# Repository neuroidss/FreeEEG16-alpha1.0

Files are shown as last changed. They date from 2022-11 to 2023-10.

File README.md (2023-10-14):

# FreeEEG16-alpha1.0 TEST FAILED
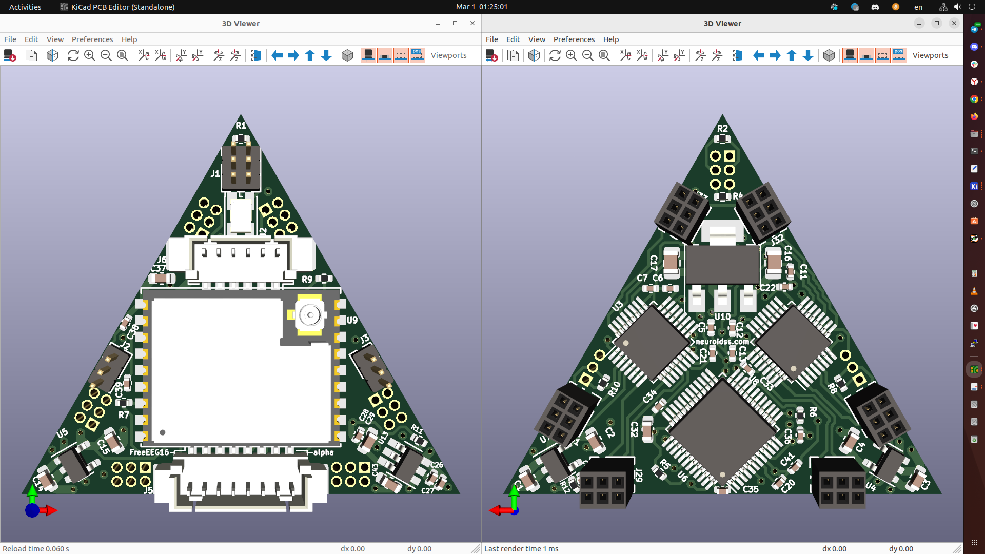
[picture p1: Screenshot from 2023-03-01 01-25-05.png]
FreeEEG16-alpha

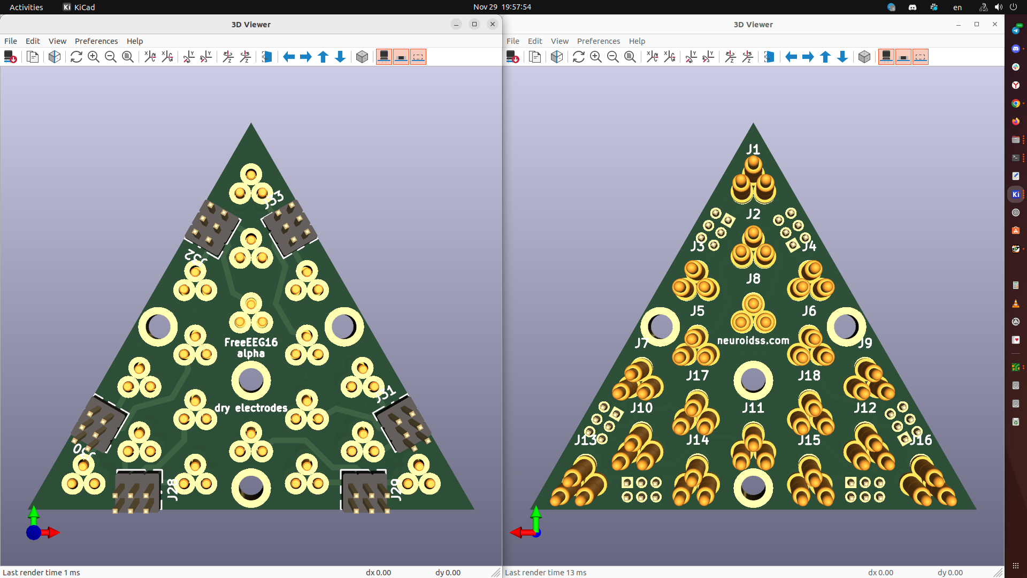
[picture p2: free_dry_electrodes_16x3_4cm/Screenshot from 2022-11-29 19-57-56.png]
free_dry_electrodes_16x3_4cm


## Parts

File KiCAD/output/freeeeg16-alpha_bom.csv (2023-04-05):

Id | Designator | Footprint | Quantity | Designation | Supplier and ref
1 | C14,C15,C3,C2,C1,C4 | C_0603_1608Metric | 6 | 2.2u | CL10A225KO8NNNC | GRM188R71A225KE15D
2 | C29,C37 | C_0603_1608Metric | 2 | 10u | GRM188R60J106ME47D
3 | R13,R9,R7 | R_0402_1005Metric | 3 | 10k | RC0402JR-0710KL
4 | C39,C27,C5,C11,C13,C7 | C_0402_1005Metric | 6 | 1u | CL05A105KO5NNNC
5 | C38,C26,C28,C36,C40,C22,C20,C35,C21,C33,C41,C34 | C_0402_1005Metric | 12 | 100n | CL05B104KO5NNNC
6 | R11,R1,R8,R4,R2,R10 | R_0402_1005Metric | 6 | 0 | RC0402JR-070RL
7 | J1 | PinHeader_2x03_P1.27mm_Vertical | 1 | Conn_02x03_Odd_Even | 20021111-00006T1LF
8 | C43 | C_0603_1608Metric | 1 | 10u DNP | DNP
9 | U5,U4,U7 | SOT-23-5 | 3 | LP5907 | LP5907MFX-3.3/NOPB
10 | U13 | SOT-23-6_Handsoldering | 1 | MAX6070AAUT12 | MAX6070AAUT12+T
11 | J5 | Molex_PicoBlade_53398-0871_1x08-1MP_P1.25mm_Vertical_cut | 1 | Conn_01x08 | 53398-0871
12 | J6 | Molex_PicoBlade_53398-0671_1x06-1MP_P1.25mm_Vertical | 1 | Conn_01x06 | 53398-0671
13 | J3,J2 | PinHeader_1x03_P1.27mm_Vertical | 2 | Conn_01x03 | TMS-103-02-L-S
14 | U2 | Oscillator_SMD_EuroQuartz_XO32-4Pin_3.2x2.5mm_HandSoldering_cut | 1 | 8.192MHz | ECS-2520MVLC-081.92-CN-TR | ECS-2520MVLC-081.92-BN-TR3 | ECS-2520MVLC-081.92-BN-TR | SIT8924BA-22-33E-8.192000G
15 | U9 | ESP32-C3-WROOM-02U | 1 | ESP32-C3-WROOM-02 | ESP32-C3-WROOM-02U-N4
16 | J29,J28,J31,J32,J33,J30 | PinSocket_2x03_P1.27mm_Vertical | 6 | Conn_02x03_Odd_Even | 20021311-00006T4LF
17 | R6,R5 | R_0402_1005Metric | 2 | 4k7 | RC0402JR-074K7L
18 | U6 | LQFP-48_7x7mm_P0.5mm | 1 | STM32F103CBTx | STM32F103C8T6 | GD32VF103CBT6 | CH32V103C8T6
19 | U10 | SOT-223-3_TabPin2 | 1 | AMS1117-3.3 | TLV1117-33IDCY | TLV1117-33IDCYG3
20 | C12,C6 | C_0402_1005Metric | 2 | 220n | CC0402KRX5R5BB224
21 | U3,U8 | LQFP-32_5x5mm_P0.5mm | 2 | ADS131M08IPBSR | ADS131M08IPBSR
22 | C16,C17 | C_0805_2012Metric | 2 | 22u | GRM21BR60J226ME39L
23 | C32 | C_0603_1608Metric | 1 | 4.7u | C0603C475K9PACTU
24 | R12 | R_0402_1005Metric | 1 | 0 DNP | DNP

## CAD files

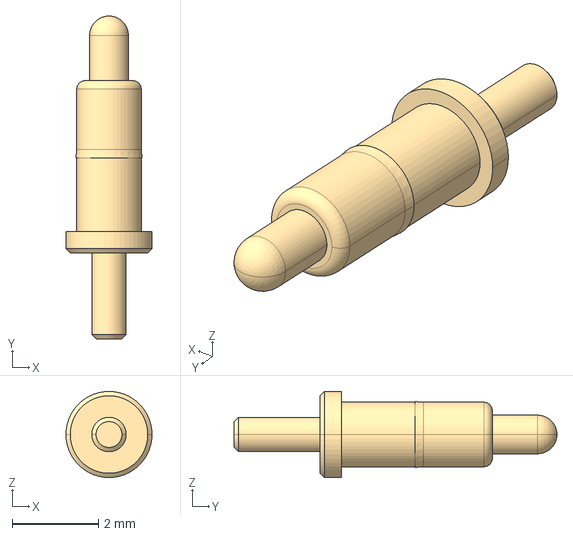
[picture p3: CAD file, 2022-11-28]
free_dry_electrodes_16x3_4cm/p70-2100045/p70-2100045.stp
2.00 x 7.50 x 2.00 mm

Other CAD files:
free_dry_electrodes_16x3_4cm/p70-2100045/p70-2100045.igs

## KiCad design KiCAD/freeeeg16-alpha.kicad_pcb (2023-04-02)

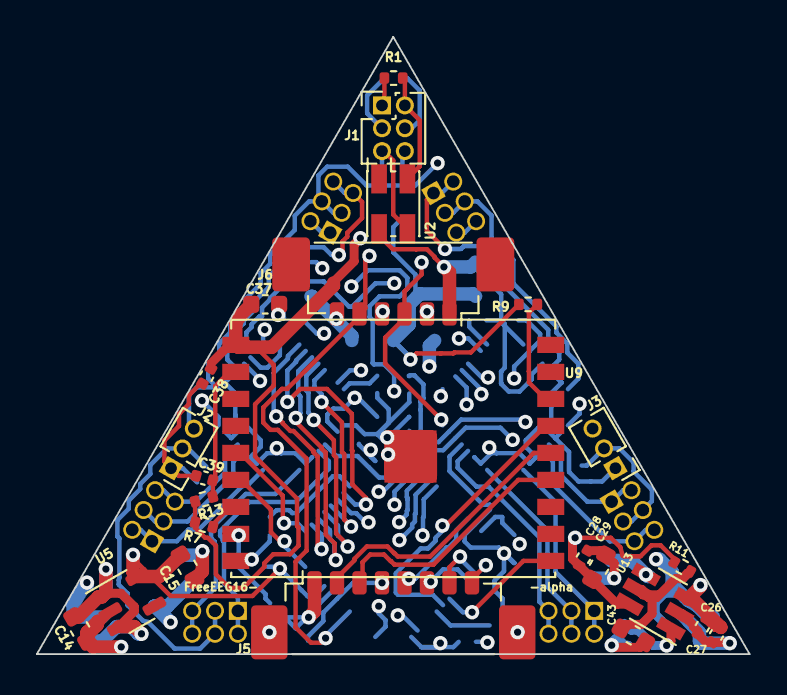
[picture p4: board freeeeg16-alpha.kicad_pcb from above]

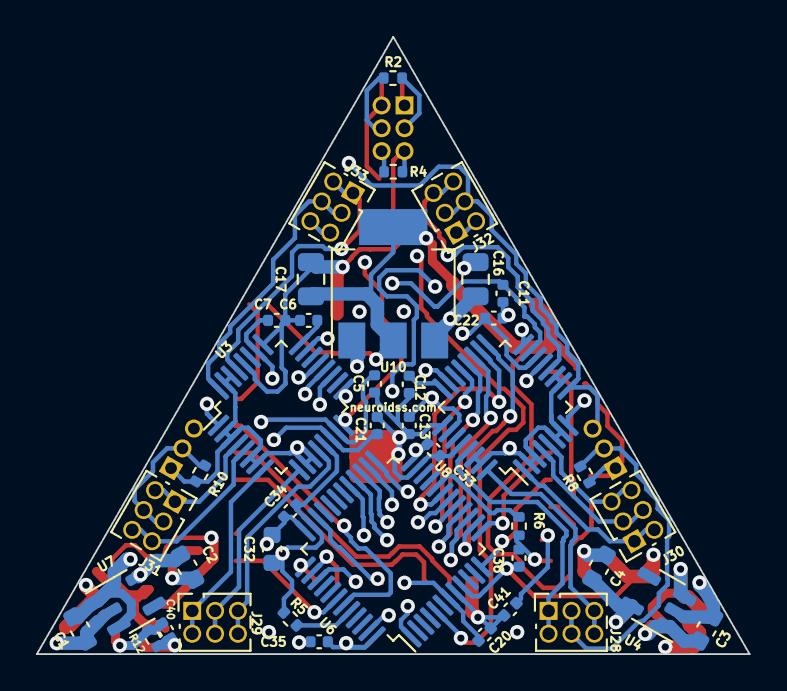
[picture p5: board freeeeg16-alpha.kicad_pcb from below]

Board: 4 copper layers, 39.6 x 34.3 mm, 65 parts (41 on the bottom side), 62 nets.

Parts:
C1, C2, C3, C4, C14, C15: 2.2u; C_0603_1608Metric
C5, C7, C11, C13, C27, C39: 1u; C_0402_1005Metric
C6, C12: 220n; C_0402_1005Metric
C16, C17: 22u; C_0805_2012Metric
C20, C21, C22, C26, C28, C33, C34, C35, C36, C38, C40, C41: 100n; C_0402_1005Metric
C29, C37: 10u; C_0603_1608Metric
C32: 4.7u; C_0603_1608Metric
C43: 10u DNP; C_0603_1608Metric
J1: Conn_02x03_Odd_Even; PinHeader_2x03_P1.27mm_Vertical
J2, J3: Conn_01x03; PinHeader_1x03_P1.27mm_Vertical
J5: Conn_01x08; Molex_PicoBlade_53398-0871_1x08-1MP_P1.25mm_Vertical_cut
J6: Conn_01x06; Molex_PicoBlade_53398-0671_1x06-1MP_P1.25mm_Vertical
J28, J29, J30, J31, J32, J33: Conn_02x03_Odd_Even; PinSocket_2x03_P1.27mm_Vertical
R1, R2, R4, R8, R10, R11: 0; R_0402_1005Metric
R5, R6: 4k7; R_0402_1005Metric
R7, R9, R13: 10k; R_0402_1005Metric
R12: 0 DNP; R_0402_1005Metric
U2: 8.192MHz; Oscillator_SMD_EuroQuartz_XO32-4Pin_3.2x2.5mm_HandSoldering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
U3, U8: ADS131M08IPBSR; LQFP-32_5x5mm_P0.5mm
U4, U5, U7: LP5907; SOT-23-5
U6: STM32F103CBTx; LQFP-48_7x7mm_P0.5mm
U9: ESP32-C3-WROOM-02; ESP32-C3-WROOM-02U
U10: AMS1117-3.3; SOT-223-3_TabPin2
U13: MAX6070AAUT12; SOT-23-6_Handsoldering

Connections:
3V3_1_IN: C1.1, C3.1, C14.1, C16.1, J6.6, U4.1 (IN), U4.3 (EN), U5.1 (IN), U5.3 (EN), U7.1 (IN), U7.3 (EN), U10.3 (VI)
3V3_2_GND: C1.2, C2.2, C3.2, C4.2, C5.2, C6.2, C7.2, C11.2, C12.2, C13.2, C14.2, C15.2, C16.2, C17.2, C20.1, C21.2, C22.2, C26.2, C27.2, C28.2, C29.2, C32.2, C33.2, C34.2, C35.2, C36.2, C37.2, C38.2, C39.1, C40.2, C41.1, C43.1, J2.1, J5.1, J6.1, R5.2, R6.2, R8.2, R12.2, U2.2 (GND), U3.13 (AGND), U3.25 (DGND), U3.28 (AGND), U4.2 (GND), U5.2 (GND), U6.8 (VSSA), U6.23 (VSS), U6.35 (VSS), U6.47 (VSS), U7.2 (GND), U8.13 (AGND), U8.25 (DGND), U8.28 (AGND), U9.9 (GND), U9.19 (GND), U10.1 (GND), U13.2 (GND)
3V3_5_OUT: C17.1, C37.1, C38.1, R7.2, R9.2, R13.2, U9.1 (3V3), U10.2 (VO)
/ADC1/24_CAP: C12.1, U8.24 (CAP)
/ADC2/24_CAP: C6.1, U3.24 (CAP)
/J17: J3.2, J31.3, J31.4, R10.1
/J18: J2.2, J28.3, J28.4, R8.1
/vref2/1_FILTER: C40.1, R12.1, U13.1 (FILTER)
ACC_5_VDDIO: C15.1, C32.1, C33.1, C34.1, C35.1, C36.1, J1.1, R1.1, U5.5 (OUT), U6.1 (VBAT), U6.9 (VDDA), U6.24 (VDD), U6.36 (VDD), U6.48 (VDD)
ACC_13_SCL: U6.42 (PB6), U9.10 (GPIO10)
ACC_14_SDA: U6.43 (PB7), U9.15 (GPIO3/ADC1_CH3)
ADC1_01_AIN2P: J30.1, J30.2, U8.1 (AIN2P)
ADC1_02_AIN2N: J3.1, J6.2, R10.2, U3.2 (AIN2N), U3.3 (AIN3N), U3.6 (AIN4N), U3.7 (AIN5N), U3.10 (AIN6N), U3.11 (AIN7N), U3.30 (AIN0N), U3.31 (AIN1N), U8.2 (AIN2N), U8.3 (AIN3N), U8.6 (AIN4N), U8.7 (AIN5N), U8.10 (AIN6N), U8.11 (AIN7N), U8.30 (AIN0N), U8.31 (AIN1N)
ADC1_04_AIN3P: J30.3, J30.4, U8.4 (AIN3P)
ADC1_05_AIN4P: J30.5, J30.6, U8.5 (AIN4P)
ADC1_08_AIN5P: J32.1, J32.2, U8.8 (AIN5P)
ADC1_09_AIN6P: J2.3, J3.3, J32.3, J32.4, U8.9 (AIN6P)
ADC1_12_AIN7P: J32.5, J32.6, U8.12 (AIN7P)
ADC1_14_REFIN: C21.1, C22.1, C28.1, C29.1, J6.4, R11.2, U3.14 (REFIN), U8.14 (REFIN), U13.6 (OUTF)
ADC1_15_AVDD: C2.1, C5.1, C11.1, C26.1, C27.1, U3.15 (AVDD), U7.5 (OUT), U8.15 (AVDD), U13.3 (EN), U13.4 (IN)
ADC1_16_SYNC/RESET: J1.4, J6.3, R2.2, U3.16 (SYNC/RESET), U8.16 (SYNC/RESET)
ADC1_17_CS: U6.14 (PA4), U8.17 (CS)
ADC1_18_DRDY: U6.19 (PB1), U8.18 (DRDY)
ADC1_19_SCLK: U6.15 (PA5), U8.19 (SCLK)
ADC1_20_DOUT: U6.16 (PA6), U8.20 (DOUT)
ADC1_21_DIN: U6.17 (PA7), U8.21 (DIN)
ADC1_23_XTAL1/CLKIN: U3.23 (XTAL1/CLKIN), U6.29 (PA8), U8.23 (XTAL1/CLKIN)
ADC1_26_DVDD: C4.1, C7.1, C13.1, U3.26 (DVDD), U4.5 (OUT), U8.26 (DVDD)
ADC1_29_AIN0P: J28.1, J28.2, U8.29 (AIN0P)
ADC1_32_AIN1P: J28.5, J28.6, U8.32 (AIN1P)
ADC2_01_AIN2P: J33.5, J33.6, U3.1 (AIN2P)
ADC2_04_AIN3P: J31.1, J31.2, U3.4 (AIN3P)
ADC2_05_AIN4P: J31.5, J31.6, U3.5 (AIN4P)
ADC2_08_AIN5P: J29.1, J29.2, U3.8 (AIN5P)
ADC2_09_AIN6P: J29.3, J29.4, U3.9 (AIN6P)
ADC2_12_AIN7P: J29.5, J29.6, U3.12 (AIN7P)
ADC2_17_CS: U3.17 (CS), U6.25 (PB12)
ADC2_19_SCLK: U3.19 (SCLK), U6.26 (PB13)
ADC2_20_DOUT: U3.20 (DOUT), U6.27 (PB14)
ADC2_21_DIN: U3.21 (DIN), U6.28 (PB15)
ADC2_29_AIN0P: J33.1, J33.2, U3.29 (AIN0P)
ADC2_32_AIN1P: J33.3, J33.4, U3.32 (AIN1P)
CRYSTAL_3_OUT: J1.5, R4.1, U2.3 (OUT)
CRYSTAL_4_Vin: J1.2, R1.2, U2.4 (Vin)
MCU_5_PDO0_RCC_OSC_IN: J1.6, J6.5, R4.2, U6.5 (PD0)
MCU_7_NRST: C20.2, J5.4, U6.7 (NRST)
MCU_12_PA2_USART2_TX: U6.12 (PA2), U9.6 (GPIO7)
MCU_13_PA3_USART2_RX: U6.13 (PA3), U9.5 (GPIO6)
MCU_18_PB0_ADC1_SYNC/RESET: J1.3, R2.1, U6.18 (PB0)
MCU_20_PB2_BOOT1: R6.1, U6.20 (PB2)
MCU_34_PA13_SYS_JTMS-SWDIO: J5.5, U6.34 (PA13)
MCU_37_PA14_SYS_JTCK-SWCLK: J5.8, U6.37 (PA14)
MCU_38_PA15_SYS_JTDI: J5.7, U6.38 (PA15)
MCU_39_PB3_SYS_JTDO-TRACESWO: J5.6, U6.39 (PB3)
MCU_44_BOOT0: R5.1, U6.44 (BOOT0)
unnamed: C43.2, R11.1, U13.5 (OUTS)
RADIO_2_EN: C39.2, R13.1, U9.2 (EN/CHIP_PU)
RADIO_7_GPIO8: R7.1, U9.7 (GPIO8)
RADIO_8_GPIO9: C41.2, U9.8 (GPIO9)
RADIO_13_GPIO18/USB_D-: J5.3, U9.13 (GPIO18/USB_D-)
RADIO_14_GPIO19/USB_D+: J5.2, U9.14 (GPIO19/USB_D+)
RADIO_16_GPIO2: R9.1, U9.16 (GPIO2/ADC1_CH2)

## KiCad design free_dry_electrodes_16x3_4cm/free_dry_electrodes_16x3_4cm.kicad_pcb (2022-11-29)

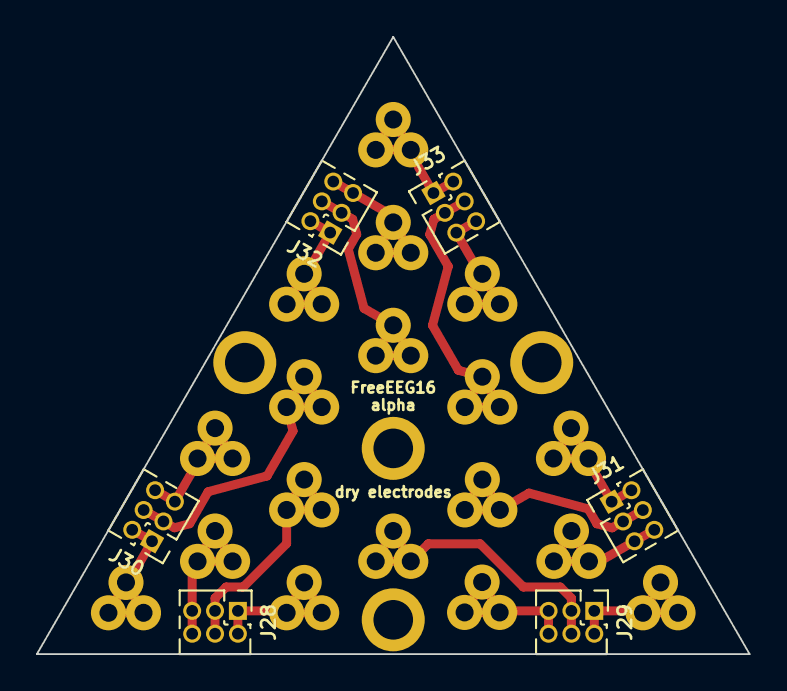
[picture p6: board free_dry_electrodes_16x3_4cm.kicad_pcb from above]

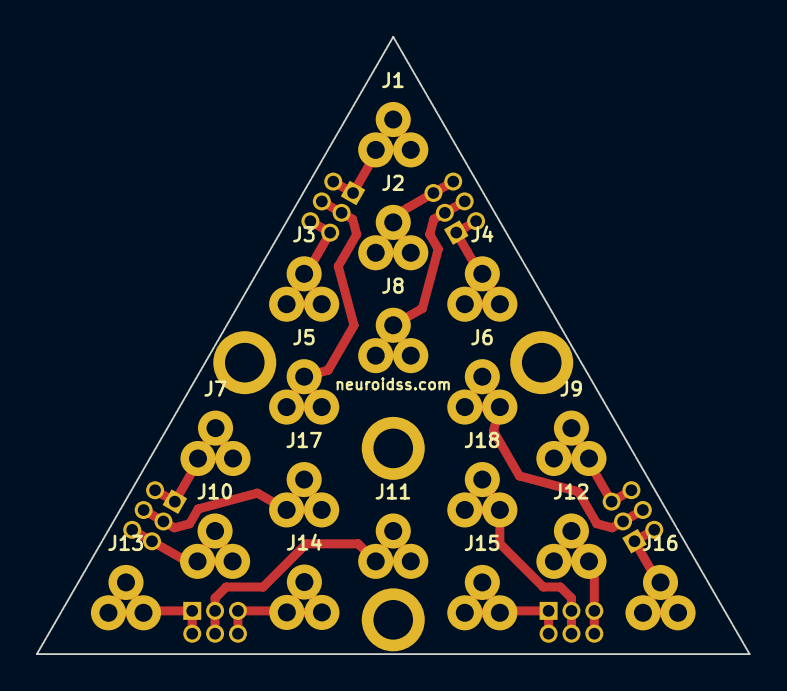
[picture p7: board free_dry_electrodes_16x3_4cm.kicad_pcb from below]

Board: 2 copper layers, 39.6 x 34.3 mm, 24 parts (18 on the bottom side), 18 nets.

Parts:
J1, J2, J3, J4, J5, J6, J7, J8, J9, J10, J11, J12, J13, J14, J15, J16, J17, J18: Conn_01x03; CPA_3_od4.5_d1.95_id1.0
J28, J29, J30, J31, J32, J33: Conn_02x03_Odd_Even; PinHeader_2x03_P1.27mm_Vertical

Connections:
/J1: J1.1, J1.2, J1.3, J33.1, J33.2
/J2: J2.1, J2.2, J2.3, J32.5, J32.6
/J3: J3.1, J3.2, J3.3, J33.5, J33.6
/J4: J4.1, J4.2, J4.3, J32.1, J32.2
/J5: J5.1, J5.2, J5.3, J33.3, J33.4
/J6: J6.1, J6.2, J6.3, J30.3, J30.4
/J7: J7.1, J7.2, J7.3, J31.1, J31.2
/J8: J8.1, J8.2, J8.3, J32.3, J32.4
/J9: J9.1, J9.2, J9.3, J30.5, J30.6
/J10: J10.1, J10.2, J10.3, J31.5, J31.6
/J11: J11.1, J11.2, J11.3, J29.3, J29.4
/J12: J12.1, J12.2, J12.3, J28.5, J28.6
/J13: J13.1, J13.2, J13.3, J29.1, J29.2
/J14: J14.1, J14.2, J14.3, J29.5, J29.6
/J15: J15.1, J15.2, J15.3, J28.1, J28.2
/J16: J16.1, J16.2, J16.3, J30.1, J30.2
/J17: J17.1, J17.2, J17.3, J31.3, J31.4
/J18: J18.1, J18.2, J18.3, J28.3, J28.4

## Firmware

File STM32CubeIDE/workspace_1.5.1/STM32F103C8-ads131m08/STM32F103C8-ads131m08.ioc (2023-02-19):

#MicroXplorer Configuration settings - do not modify
Dma.Request0=USART2_TX
Dma.Request1=USART2_RX
Dma.Request2=SPI1_RX
Dma.Request3=SPI1_TX
Dma.Request4=SPI2_RX
Dma.Request5=SPI2_TX
Dma.RequestsNb=6
Dma.SPI1_RX.2.Direction=DMA_PERIPH_TO_MEMORY
Dma.SPI1_RX.2.Instance=DMA1_Channel2
Dma.SPI1_RX.2.MemDataAlignment=DMA_MDATAALIGN_BYTE
Dma.SPI1_RX.2.MemInc=DMA_MINC_ENABLE
Dma.SPI1_RX.2.Mode=DMA_NORMAL
Dma.SPI1_RX.2.PeriphDataAlignment=DMA_PDATAALIGN_BYTE
Dma.SPI1_RX.2.PeriphInc=DMA_PINC_DISABLE
Dma.SPI1_RX.2.Priority=DMA_PRIORITY_LOW
Dma.SPI1_RX.2.RequestParameters=Instance,Direction,PeriphInc,MemInc,PeriphDataAlignment,MemDataAlignment,Mode,Priority
Dma.SPI1_TX.3.Direction=DMA_MEMORY_TO_PERIPH
Dma.SPI1_TX.3.Instance=DMA1_Channel3
Dma.SPI1_TX.3.MemDataAlignment=DMA_MDATAALIGN_BYTE
Dma.SPI1_TX.3.MemInc=DMA_MINC_ENABLE
Dma.SPI1_TX.3.Mode=DMA_NORMAL
Dma.SPI1_TX.3.PeriphDataAlignment=DMA_PDATAALIGN_BYTE
Dma.SPI1_TX.3.PeriphInc=DMA_PINC_DISABLE
Dma.SPI1_TX.3.Priority=DMA_PRIORITY_LOW
Dma.SPI1_TX.3.RequestParameters=Instance,Direction,PeriphInc,MemInc,PeriphDataAlignment,MemDataAlignment,Mode,Priority
Dma.SPI2_RX.4.Direction=DMA_PERIPH_TO_MEMORY
Dma.SPI2_RX.4.Instance=DMA1_Channel4
Dma.SPI2_RX.4.MemDataAlignment=DMA_MDATAALIGN_BYTE
Dma.SPI2_RX.4.MemInc=DMA_MINC_ENABLE
Dma.SPI2_RX.4.Mode=DMA_NORMAL
Dma.SPI2_RX.4.PeriphDataAlignment=DMA_PDATAALIGN_BYTE
Dma.SPI2_RX.4.PeriphInc=DMA_PINC_DISABLE
Dma.SPI2_RX.4.Priority=DMA_PRIORITY_LOW
Dma.SPI2_RX.4.RequestParameters=Instance,Direction,PeriphInc,MemInc,PeriphDataAlignment,MemDataAlignment,Mode,Priority
Dma.SPI2_TX.5.Direction=DMA_MEMORY_TO_PERIPH
Dma.SPI2_TX.5.Instance=DMA1_Channel5
Dma.SPI2_TX.5.MemDataAlignment=DMA_MDATAALIGN_BYTE
Dma.SPI2_TX.5.MemInc=DMA_MINC_ENABLE
Dma.SPI2_TX.5.Mode=DMA_NORMAL
Dma.SPI2_TX.5.PeriphDataAlignment=DMA_PDATAALIGN_BYTE
Dma.SPI2_TX.5.PeriphInc=DMA_PINC_DISABLE
Dma.SPI2_TX.5.Priority=DMA_PRIORITY_LOW
Dma.SPI2_TX.5.RequestParameters=Instance,Direction,PeriphInc,MemInc,PeriphDataAlignment,MemDataAlignment,Mode,Priority
Dma.USART2_RX.1.Direction=DMA_PERIPH_TO_MEMORY
Dma.USART2_RX.1.Instance=DMA1_Channel6
Dma.USART2_RX.1.MemDataAlignment=DMA_MDATAALIGN_BYTE
Dma.USART2_RX.1.MemInc=DMA_MINC_ENABLE
Dma.USART2_RX.1.Mode=DMA_CIRCULAR
Dma.USART2_RX.1.PeriphDataAlignment=DMA_PDATAALIGN_BYTE
Dma.USART2_RX.1.PeriphInc=DMA_PINC_DISABLE
Dma.USART2_RX.1.Priority=DMA_PRIORITY_LOW
Dma.USART2_RX.1.RequestParameters=Instance,Direction,PeriphInc,MemInc,PeriphDataAlignment,MemDataAlignment,Mode,Priority
Dma.USART2_TX.0.Direction=DMA_MEMORY_TO_PERIPH
Dma.USART2_TX.0.Instance=DMA1_Channel7
Dma.USART2_TX.0.MemDataAlignment=DMA_MDATAALIGN_BYTE
Dma.USART2_TX.0.MemInc=DMA_MINC_ENABLE
Dma.USART2_TX.0.Mode=DMA_NORMAL
Dma.USART2_TX.0.PeriphDataAlignment=DMA_PDATAALIGN_BYTE
Dma.USART2_TX.0.PeriphInc=DMA_PINC_DISABLE
Dma.USART2_TX.0.Priority=DMA_PRIORITY_LOW
Dma.USART2_TX.0.RequestParameters=Instance,Direction,PeriphInc,MemInc,PeriphDataAlignment,MemDataAlignment,Mode,Priority
File.Version=6
GPIO.groupedBy=Group By Peripherals
I2C1.I2C_Mode=I2C_Standard
I2C1.IPParameters=I2C_Mode
KeepUserPlacement=false
Mcu.Family=STM32F1
Mcu.IP0=DMA
Mcu.IP1=I2C1
Mcu.IP2=NVIC
Mcu.IP3=RCC
Mcu.IP4=SPI1
Mcu.IP5=SPI2
Mcu.IP6=SYS
Mcu.IP7=USART1
Mcu.IP8=USART2
Mcu.IP9=USART3
Mcu.IPNb=10
Mcu.Name=STM32F103C(8-B)Tx
Mcu.Package=LQFP48
Mcu.Pin0=PD0-OSC_IN
Mcu.Pin1=PD1-OSC_OUT
Mcu.Pin10=PB2
Mcu.Pin11=PB10
Mcu.Pin12=PB11
Mcu.Pin13=PB12
Mcu.Pin14=PB13
Mcu.Pin15=PB14
Mcu.Pin16=PB15
Mcu.Pin17=PA8
Mcu.Pin18=PA9
Mcu.Pin19=PA10
Mcu.Pin2=PA2
Mcu.Pin20=PA13
Mcu.Pin21=PA14
Mcu.Pin22=PA15
Mcu.Pin23=PB3
Mcu.Pin24=PB6
Mcu.Pin25=PB7
Mcu.Pin26=VP_SYS_VS_Systick
Mcu.Pin3=PA3
Mcu.Pin4=PA4
Mcu.Pin5=PA5
Mcu.Pin6=PA6
Mcu.Pin7=PA7
Mcu.Pin8=PB0
Mcu.Pin9=PB1
Mcu.PinsNb=27
Mcu.ThirdPartyNb=0
Mcu.UserConstants=
Mcu.UserName=STM32F103C8Tx
MxCube.Version=6.1.1
MxDb.Version=DB.6.0.10
NVIC.BusFault_IRQn=true\:0\:0\:false\:false\:true\:false\:false
NVIC.DMA1_Channel2_IRQn=true\:0\:0\:false\:false\:true\:false\:true
NVIC.DMA1_Channel3_IRQn=true\:0\:0\:false\:false\:true\:false\:true
NVIC.DMA1_Channel4_IRQn=true\:0\:0\:false\:false\:true\:false\:true
NVIC.DMA1_Channel5_IRQn=true\:0\:0\:false\:false\:true\:false\:true
NVIC.DMA1_Channel6_IRQn=true\:0\:0\:false\:false\:true\:false\:true
NVIC.DMA1_Channel7_IRQn=true\:0\:0\:false\:false\:true\:false\:true
NVIC.DebugMonitor_IRQn=true\:0\:0\:false\:false\:true\:false\:false
NVIC.EXTI1_IRQn=true\:0\:0\:false\:false\:true\:true\:true
NVIC.ForceEnableDMAVector=true
NVIC.HardFault_IRQn=true\:0\:0\:false\:false\:true\:false\:false
NVIC.I2C1_ER_IRQn=true\:0\:0\:false\:false\:true\:true\:true
NVIC.I2C1_EV_IRQn=true\:0\:0\:false\:false\:true\:true\:true
NVIC.MemoryManagement_IRQn=true\:0\:0\:false\:false\:true\:false\:false
NVIC.NonMaskableInt_IRQn=true\:0\:0\:false\:false\:true\:false\:false
NVIC.PVD_IRQn=true\:0\:0\:false\:false\:true\:true\:true
NVIC.PendSV_IRQn=true\:0\:0\:false\:false\:true\:false\:false
NVIC.PriorityGroup=NVIC_PRIORITYGROUP_4
NVIC.SPI1_IRQn=true\:0\:0\:false\:false\:true\:true\:true
NVIC.SPI2_IRQn=true\:0\:0\:false\:false\:true\:true\:true
NVIC.SVCall_IRQn=true\:0\:0\:false\:false\:true\:false\:false
NVIC.SysTick_IRQn=true\:0\:0\:false\:false\:true\:false\:true
NVIC.USART1_IRQn=true\:0\:0\:false\:false\:true\:true\:true
NVIC.USART2_IRQn=true\:0\:0\:false\:false\:true\:true\:true
NVIC.UsageFault_IRQn=true\:0\:0\:false\:false\:true\:false\:false
PA10.Mode=Asynchronous
PA10.Signal=USART1_RX
PA13.Mode=JTAG_4_pins
PA13.Signal=SYS_JTMS-SWDIO
PA14.Mode=JTAG_4_pins
PA14.Signal=SYS_JTCK-SWCLK
PA15.Mode=JTAG_4_pins
PA15.Signal=SYS_JTDI
PA2.Mode=Asynchronous
PA2.Signal=USART2_TX
PA3.Mode=Asynchronous
PA3.Signal=USART2_RX
PA4.GPIOParameters=GPIO_Speed,PinState,GPIO_Label
PA4.GPIO_Label=SPI1_NSS
PA4.GPIO_Speed=GPIO_SPEED_FREQ_HIGH
PA4.Locked=true
PA4.PinState=GPIO_PIN_SET
PA4.Signal=GPIO_Output
PA5.Mode=Full_Duplex_Master
PA5.Signal=SPI1_SCK
PA6.Mode=Full_Duplex_Master
PA6.Signal=SPI1_MISO
PA7.Mode=Full_Duplex_Master
PA7.Signal=SPI1_MOSI
PA8.Mode=Clock-out
PA8.Signal=RCC_MCO
PA9.Mode=Asynchronous
PA9.Signal=USART1_TX
PB0.GPIOParameters=GPIO_Label
PB0.GPIO_Label=ADC1_SYNC_RESET
PB0.Locked=true
PB0.Signal=GPIO_Output
PB1.GPIOParameters=GPIO_Label
PB1.GPIO_Label=ADC1_DRDY
PB1.Locked=true
PB1.Signal=GPXTI1
PB10.Mode=Asynchronous
PB10.Signal=USART3_TX
PB11.Mode=Asynchronous
PB11.Signal=USART3_RX
PB12.GPIOParameters=GPIO_Speed,PinState,GPIO_Label
PB12.GPIO_Label=SPI2_NSS
PB12.GPIO_Speed=GPIO_SPEED_FREQ_HIGH
PB12.Locked=true
PB12.PinState=GPIO_PIN_SET
PB12.Signal=GPIO_Output
PB13.Mode=Full_Duplex_Master
PB13.Signal=SPI2_SCK
PB14.Mode=Full_Duplex_Master
PB14.Signal=SPI2_MISO
PB15.Mode=Full_Duplex_Master
PB15.Signal=SPI2_MOSI
PB2.GPIOParameters=GPIO_Label
PB2.GPIO_Label=BOOT1
PB2.Locked=true
PB2.Signal=GPIO_Input
PB3.Mode=JTAG_4_pins
PB3.Signal=SYS_JTDO-TRACESWO
PB6.Mode=I2C
PB6.Signal=I2C1_SCL
PB7.Mode=I2C
PB7.Signal=I2C1_SDA
PD0-OSC_IN.Mode=HSE-External-Clock-Source
PD0-OSC_IN.Signal=RCC_OSC_IN
PD1-OSC_OUT.Mode=HSE-External-Clock-Source
PD1-OSC_OUT.Signal=RCC_OSC_OUT
PinOutPanel.RotationAngle=0
ProjectManager.AskForMigrate=true
ProjectManager.BackupPrevious=false
ProjectManager.CompilerOptimize=6
ProjectManager.ComputerToolchain=false
ProjectManager.CoupleFile=false
ProjectManager.CustomerFirmwarePackage=
ProjectManager.DefaultFWLocation=true
ProjectManager.DeletePrevious=true
ProjectManager.DeviceId=STM32F103C8Tx
ProjectManager.FirmwarePackage=STM32Cube FW_F1 V1.8.4
ProjectManager.FreePins=false
ProjectManager.HalAssertFull=false
ProjectManager.HeapSize=0x200
ProjectManager.KeepUserCode=true
ProjectManager.LastFirmware=true
ProjectManager.LibraryCopy=1
ProjectManager.MainLocation=Core/Src
ProjectManager.NoMain=false
ProjectManager.PreviousToolchain=
ProjectManager.ProjectBuild=false
ProjectManager.ProjectFileName=STM32F103C8-ads131m08.ioc
ProjectManager.ProjectName=STM32F103C8-ads131m08
ProjectManager.RegisterCallBack=
ProjectManager.StackSize=0x400
ProjectManager.TargetToolchain=STM32CubeIDE
ProjectManager.ToolChainLocation=
ProjectManager.UnderRoot=true
ProjectManager.functionlistsort=1-MX_GPIO_Init-GPIO-false-HAL-true,2-MX_DMA_Init-DMA-false-HAL-true,3-SystemClock_Config-RCC-false-HAL-false,4-MX_SPI1_Init-SPI1-false-HAL-true,5-MX_SPI2_Init-SPI2-false-HAL-true,6-MX_USART2_UART_Init-USART2-false-HAL-true,7-MX_USART1_UART_Init-USART1-false-HAL-true,8-MX_USART3_UART_Init-USART3-false-HAL-true,9-MX_I2C1_Init-I2C1-false-HAL-true
RCC.ADCFreqValue=32768000
RCC.AHBFreq_Value=65536000
RCC.APB1CLKDivider=RCC_HCLK_DIV2
RCC.APB1Freq_Value=32768000
RCC.APB1TimFreq_Value=65536000
RCC.APB2Freq_Value=65536000
RCC.APB2TimFreq_Value=65536000
RCC.FCLKCortexFreq_Value=65536000
RCC.FamilyName=M
RCC.HCLKFreq_Value=65536000
RCC.HSEDivPLL=RCC_HSE_PREDIV_DIV2
RCC.HSE_VALUE=8192000
RCC.IPParameters=ADCFreqValue,AHBFreq_Value,APB1CLKDivider,APB1Freq_Value,APB1TimFreq_Value,APB2Freq_Value,APB2TimFreq_Value,FCLKCortexFreq_Value,FamilyName,HCLKFreq_Value,HSEDivPLL,HSE_VALUE,MCOFreq_Value,PLLCLKFreq_Value,PLLMCOFreq_Value,PLLMUL,PLLSourceVirtual,RCC_MCOSource,SYSCLKFreq_VALUE,SYSCLKSource,TimSysFreq_Value,USBFreq_Value,VCOOutput2Freq_Value
RCC.MCOFreq_Value=8192000
RCC.PLLCLKFreq_Value=65536000
RCC.PLLMCOFreq_Value=32768000
RCC.PLLMUL=RCC_PLL_MUL16
RCC.PLLSourceVirtual=RCC_PLLSOURCE_HSE
RCC.RCC_MCOSource=RCC_MCO1SOURCE_HSE
RCC.SYSCLKFreq_VALUE=65536000
RCC.SYSCLKSource=RCC_SYSCLKSOURCE_PLLCLK
RCC.TimSysFreq_Value=65536000
RCC.USBFreq_Value=65536000
RCC.VCOOutput2Freq_Value=4096000
SH.GPXTI1.0=GPIO_EXTI1
SH.GPXTI1.ConfNb=1
SPI1.BaudRatePrescaler=SPI_BAUDRATEPRESCALER_8
SPI1.CLKPhase=SPI_PHASE_2EDGE
SPI1.CLKPolarity=SPI_POLARITY_LOW
SPI1.CalculateBaudRate=8.192 MBits/s
SPI1.Direction=SPI_DIRECTION_2LINES
SPI1.IPParameters=VirtualType,Mode,Direction,CalculateBaudRate,BaudRatePrescaler,CLKPhase,CLKPolarity
SPI1.Mode=SPI_MODE_MASTER
SPI1.VirtualType=VM_MASTER
SPI2.BaudRatePrescaler=SPI_BAUDRATEPRESCALER_4
SPI2.CLKPhase=SPI_PHASE_2EDGE
SPI2.CLKPolarity=SPI_POLARITY_LOW
SPI2.CalculateBaudRate=8.192 MBits/s
SPI2.Direction=SPI_DIRECTION_2LINES
SPI2.IPParameters=VirtualType,Mode,Direction,CalculateBaudRate,BaudRatePrescaler,CLKPhase,CLKPolarity
SPI2.Mode=SPI_MODE_MASTER
SPI2.VirtualType=VM_MASTER
USART1.IPParameters=VirtualMode
USART1.VirtualMode=VM_ASYNC
USART2.BaudRate=921600
USART2.IPParameters=VirtualMode,BaudRate
USART2.VirtualMode=VM_ASYNC
USART3.IPParameters=VirtualMode
USART3.VirtualMode=VM_ASYNC
VP_SYS_VS_Systick.Mode=SysTick
VP_SYS_VS_Systick.Signal=SYS_VS_Systick
board=custom
isbadioc=false

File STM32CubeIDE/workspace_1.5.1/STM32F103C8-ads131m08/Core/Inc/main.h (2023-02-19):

/* USER CODE BEGIN Header */
/**
  ******************************************************************************
  * @file           : main.h
  * @brief          : Header for main.c file.
  *                   This file contains the common defines of the application.
  ******************************************************************************
  * @attention
  *
  * <h2><center>&copy; Copyright (c) 2023 STMicroelectronics.
  * All rights reserved.</center></h2>
  *
  * This software component is licensed by ST under BSD 3-Clause license,
  * the "License"; You may not use this file except in compliance with the
  * License. You may obtain a copy of the License at:
  *                        opensource.org/licenses/BSD-3-Clause
  *
  ******************************************************************************
  */
/* USER CODE END Header */

/* Define to prevent recursive inclusion -------------------------------------*/
#ifndef __MAIN_H
#define __MAIN_H

#ifdef __cplusplus
extern "C" {
#endif

/* Includes ------------------------------------------------------------------*/
#include "stm32f1xx_hal.h"

/* Private includes ----------------------------------------------------------*/
/* USER CODE BEGIN Includes */

/* USER CODE END Includes */

/* Exported types ------------------------------------------------------------*/
/* USER CODE BEGIN ET */

/* USER CODE END ET */

/* Exported constants --------------------------------------------------------*/
/* USER CODE BEGIN EC */

/* USER CODE END EC */

/* Exported macro ------------------------------------------------------------*/
/* USER CODE BEGIN EM */

/* USER CODE END EM */

/* Exported functions prototypes ---------------------------------------------*/
void Error_Handler(void);

/* USER CODE BEGIN EFP */

/* USER CODE END EFP */

/* Private defines -----------------------------------------------------------*/
#define SPI1_NSS_Pin GPIO_PIN_4
#define SPI1_NSS_GPIO_Port GPIOA
#define ADC1_SYNC_RESET_Pin GPIO_PIN_0
#define ADC1_SYNC_RESET_GPIO_Port GPIOB
#define ADC1_DRDY_Pin GPIO_PIN_1
#define ADC1_DRDY_GPIO_Port GPIOB
#define ADC1_DRDY_EXTI_IRQn EXTI1_IRQn
#define BOOT1_Pin GPIO_PIN_2
#define BOOT1_GPIO_Port GPIOB
#define SPI2_NSS_Pin GPIO_PIN_12
#define SPI2_NSS_GPIO_Port GPIOB
/* USER CODE BEGIN Private defines */

#define SPI1_NSS_Pin GPIO_PIN_4
#define SPI1_NSS_GPIO_Port GPIOA
#define SPI2_NSS_Pin GPIO_PIN_12
#define SPI2_NSS_GPIO_Port GPIOB
//#define SPI1_NSS2_Pin GPIO_PIN_1
//#define SPI1_NSS2_GPIO_Port GPIOB

#define FREEEEG16_ADS131M08_SPI_OPENVIBE_FREEEEG16_CONFIG_INT              (1LL<<4)

//#define FREEEEG16_IN (0)

#define FREEEEG16_IN FREEEEG16_ADS131M08_SPI_OPENVIBE_FREEEEG16_CONFIG_INT

#define FREESMARTEEG_RECEIVE_UART1  (1<<0)
#define FREESMARTEEG_RECEIVE_UART2  (1<<1)
#define FREESMARTEEG_RECEIVE_I2C1  (1<<1)
//#define FREESMARTEEG_RECEIVE FREESMARTEEG_RECEIVE_UART1
#define FREESMARTEEG_RECEIVE FREESMARTEEG_RECEIVE_UART2
//#define FREESMARTEEG_RECEIVE FREESMARTEEG_RECEIVE_I2C1

#define UART_RECEIVE_DMA (1)
//#define UART_RECEIVE_DMA (0)

//#define UART_RECEIVE_DMA_CIRCULAR (0)
#define UART_RECEIVE_DMA_CIRCULAR (1)

//#define I2C_RECEIVE_DMA (1)
#define I2C_RECEIVE_DMA (0)

#define FREEEEG16_TEST_COUNTER              (1LL<<4)
#define FREEEEG16_ADS131M08_SPI_TEST_SAMPLE_COUNT_INT (1LL<<5)
#define FREEEEG16_ADS131M08_SPI_TEXT_UART_INT (1LL<<6)
#define FREEEEG16_ADS131M08_SPI_OPENVIBE_FREEEEG16_CUSTOM_INT (1LL<<7)
#define FREEEEG16_ADS131M08_SPI_TEST_REGISTERS_INT (1LL<<8)
#define FREEEEG16_ADS131M08_SPI_SAMPLECOUNT_INT (1LL<<9)
#define FREEEEG16_TEXT_UART_CONFIG (1LL<<10)

//#define FREEEEG16_OUT (0)

//#define FREEEEG16_OUT FREEEEG16_TEST_COUNTER
//#define FREEEEG16_OUT FREEEEG16_ADS131M08_SPI_TEST_SAMPLE_COUNT_INT
//#define FREEEEG16_OUT FREEEEG16_ADS131M08_SPI_TEST_REGISTERS_INT
//#define FREEEEG16_OUT FREEEEG16_ADS131M08_SPI_TEXT_UART_INT
//#define FREEEEG16_OUT (FREEEEG16_ADS131M08_SPI_TEXT_UART_INT | FREEEEG16_TEXT_UART_CONFIG)
#define FREEEEG16_OUT FREEEEG16_ADS131M08_SPI_OPENVIBE_FREEEEG16_CUSTOM_INT
//#define FREEEEG16_OUT FREEEEG16_ADS131M08_SPI_SAMPLECOUNT_INT

#define FREESMARTEEG_ADC_NONE (0)
#define FREESMARTEEG_ADC_ADS131M08_SPI_READ_INT (1LL<<15)

#define FREESMARTEEG_ADC FREESMARTEEG_ADC_ADS131M08_SPI_READ_INT

#define FREESMARTEEG_SEND_UART1  (1<<0)
#define FREESMARTEEG_SEND_UART2  (1<<1)
//#define FREESMARTEEG_SEND FREESMARTEEG_SEND_UART1
#define FREESMARTEEG_SEND FREESMARTEEG_SEND_UART2

#define UART_DMA (1)
//#define UART_DMA (0)
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

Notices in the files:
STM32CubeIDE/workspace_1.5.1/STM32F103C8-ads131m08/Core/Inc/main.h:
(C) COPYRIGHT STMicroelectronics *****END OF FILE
